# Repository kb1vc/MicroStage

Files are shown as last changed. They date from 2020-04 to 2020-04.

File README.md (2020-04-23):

# Description:

  Micro-positioning stage. 
 
  Author: Matt Reilly

  A simple sliding table that can be positioned via a 4-40 or M3 screw. 
  
  It requires a 3D printer and a Flavia stick.  The stick is used for
  the linear bearing.  Other things might suffice, but I had some of
  these around.  

  This is what a Flavia stick looks like: 
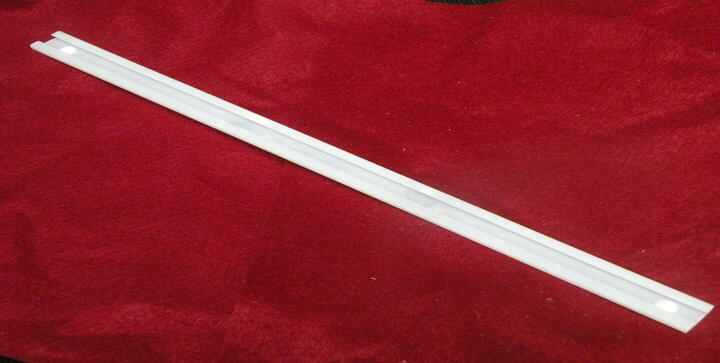
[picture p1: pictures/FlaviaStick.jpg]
A Flavia Stick
  
  
  This is a single-axis version of the micro positioning stage. 
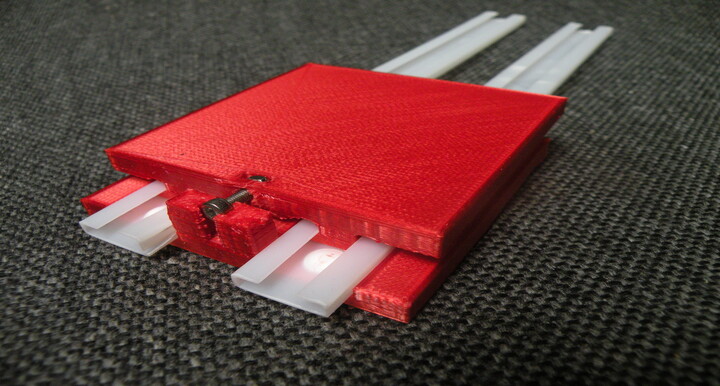
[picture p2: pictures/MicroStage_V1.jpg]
The Stage
  

  And here is an XY positioner.  
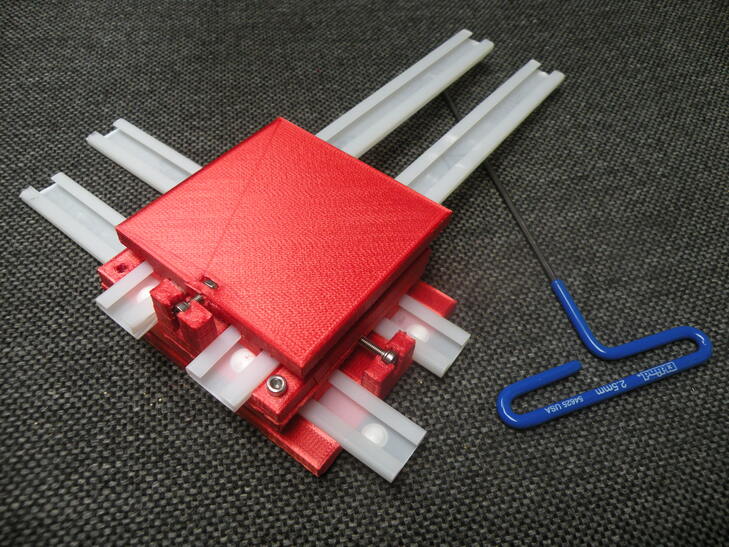
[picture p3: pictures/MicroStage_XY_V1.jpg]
XY Positioner
  
  
# The Source

The source for the components is in OpenSCAD (http://www.openscad.org). It 
is better than STL for distribution, as normal humans can read and write it.

I try to provide some commentary in the source code where things aren't 
obvious or where I expect you'd want to make some changes.  Most of the
good comments are in Common.scad where all the dimensions are defined. 

# Printing

The prototypes and test widgets were printed on a Monoprice Maker Select Plus
using Silk PLA at 230C. The slide was printed flat side up, sitting on the four 
feet. This provides better dimensional control of the horizontal parts of 
the feet which must fit nicely inside the Flavia sticks. 

I used Cura version 3.6 for the slicer. (Yes, I know they're on to newer 
versions, but 3.6 works and I don't have to worry about losing a lot of
configuration data.)  The infill density was 30% and the support density 
was 10%.  YMMV and I didn't do an exhaustive study to find the perfect
combination.  

# Dimensions

All dimensions are in inches, since that's what I have in the way of
calipers.  Yes, it is kinda 19th century, but I've got a 21st century
computer in front of me that can multiply and divide by 25.4. 

That said, the models here are all set up for M3-0.5 screws.  That gets
you 500 microns per turn of the setscrew. Skip the coffee tomorrow morning
and you might get 10 micron resolution.  If you are reading this in 
black and white, then you may only have access to imperial hardware. 
A 4-40 screw and nut will work just fine. You'll get about 25 mils per turn
which ain't so bad for something you made in your basement. 

# Assembly

Pretty much as in the picture.  (See the picture. The background is the
seat cushion on my lab chair. Sometimes I use red felt, but the shiny 
red plastic doesn't show up so well.)  The design files here have added 
mounting holes at the corners of the base and slide.  This allows you to 
bolt a Y axis base onto an X axis slide, giving you *two* dimensions to 
fiddle.

I've found that cyanoacrylate will hold the Flavia sticks to the PLA. 
I wouldn't [hang a man in a hardhat from it,](https://www.youtube.com/watch?v=sZB7sO5ZoV8) but the bond is serviceable. 

# Performance

This is not a laboratory grade device.  It does work. (Or at least the single
axis version works.  The printer isn't done with the second set of parts yet.)
The lash in the movement isn't going to worry the folks at
Starrett any time soon.  If you obsess about such things, turn the
drive screw CCW to push the table *away* from the riser block.  Then turn
the screw head CW to draw the table *toward* the riser block. That
will probably get you the smoothest motion. 

If that isn't adequate, then a trip to Ebay will probably get you 
something that even the most discerning user would find suitable. 

There is no displacement indicator -- an indicator is superfluous for my 
purposes.  If it is important to you, I would encourage you to either
1. Design a solution and try it out.  When it works, post it to github. 
2. Take a look on Ebay where you will probably find something that 
even the most discerning user would find suitable. 

The travel is limited to the length of the "leadscrew."  The assortment
I bought from the "High Precision Machine Parts and Screen Door Company of Guangzhou" topped out at 20mm.  However, [Grainger](https://www.grainger.com/product/FABORY-M3-0-50mm-Machine-Screw-38EA26) has graciously offered to supply
me with 50mm screws for a modest charge. I suspect you could make 
similar arrangements. 

# Q and A

**Q:** Why a normal screw and not a threaded rod?

**A:** A threaded rod would be ideal, but small diameter threaded rod is hard to find. Much of the stuff you find on Amazon and other places will be threaded at the ends.  (I think the intended use is for servo linkages.)  One could thread a rod with things found around the house, but life expectancies being what they are, I can't see it myself. 

**Q:** Why is it so small? 

**A:** I wanted this to be easy to print. This fits on every 3D printer that I know. 

**Q:** How long will this take to print? 

**A:** It all depends on your printer.  I printed both pieces on my well-worn Monoprice Select Plus at 0.15mm resolution in a little over 4 hours. 

**Q:** Why a pocket for the lead screw head, rather than a hole. 

**A:** Materials, variations in printer quality, phase of moon, and a 
million other things conspire to make close tolerances hard to achieve with
a typical home 3D printer.  Since
the hole in the base block would need to line up pretty closely with the
hole in the slide, all of those variations would need to be controlled. 
Counting on that is just bad engineering. 

When you hear someone say "the device is built to exacting tolerances: 
every part must be *exactly* the right size" you are either hearing 
* someone who is talking through their pants
* a sales pitch for a luxury item whose cost and price appeal to a certain kind of person
* a description of a precision device that you will never be able to afford
* a story about crap engineering by people who are too lazy to think about reality and are willing to either endure lots of rejects at the end of the line, or are going to use you for "quality" control. 

Good engineering will design within the capabilities of the technology and
the properties of the material.  I'm not a professional Mech-E, but I respect
them enough to at least *try*. 

**Q:** Will this work with ABS? PETG? Mother-of-pearl? 

**A:** I haven't tried it.  Someone should. (Well, maybe not with mother-of-pearl.)

**Q:** Why do this? 

**A:** I've got a 3D printer.  You've probably got a 3D printer.  How many tiny plastic boats does one person *need*?

**Q:** How can I prepare for an exciting career in the world of mobile pet grooming? 

**A:** I can't help you there. 

# License
See the LICENSE file for copyright and conditions for re-use.

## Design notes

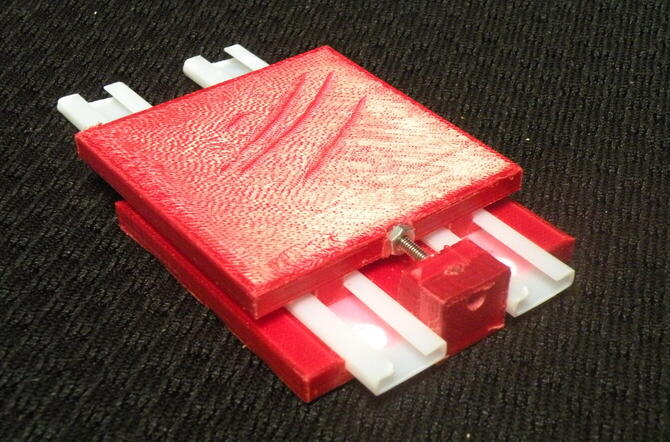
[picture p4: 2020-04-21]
pictures/MicroStage_V0.jpg

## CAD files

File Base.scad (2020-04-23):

include <Common.scad>

module BaseBlock() {
   cube([BaseW, BaseL, BaseT], center=true);
}

module Slot() {
   // a box around a flavia stick
   translate([0, 0, SlotZ]) {
      cube([FlaviaOW, BaseL * 1.1, FlaviaOH], center=true);
   }
}

module ScrewSlot(screw_dia, head_dia, head_depth, driver_dia, height) {
   // cut a slot (rather than a hole) in the riser block
   // to hold the leadscrew.  The leadscrew head will "float"
   // in the Z direction, relative to the slide to relieve
   // binding.
   //
   // There are three parts: the slot for the leadscrew threaded
   // part, the slot for the head, and the slot for the driver.
   //
   // For now, we'll do the metric M3 capscrew
   //
   // This slot is -- subtracted -- from the riser body.
   
   // The screw slot
   translate([0, 0.5 * height, 0]) cube([screw_dia, height, height], center=true);
   // the head slot
   cube([head_dia, head_depth, height], center=true);   
   // the driver slot
   translate([0, -0.5 * height, 0]) cube([driver_dia, height, height], center=true);
}


module RiserBlock() {
   difference() {
     cube([RiserW, RiserD, RiserH], center=true);
     union() {
       translate([0,0,RiserLeadScrewCenter - 0.5 * RiserH]) {
         ScrewSlot(RiserScrewHole, HeadSlotM3, HeadDM3, ShankM3, RiserD * 3);
       }
     }
   }
}

module Base() {
   translate([0,-0.5 * (BaseL - RiserD),0.5 * RiserH])
       RiserBlock();
   translate([0,0,0.5*BaseT])
   difference() {
       BaseBlock();	        
       union() { 
         translate([SlotSp * 1, 0, 0]) Slot();
         translate([-SlotSp * 1, 0, 0]) Slot();
	 MountingHoles();
       }
   }
}

scale([25.4,25.4,25.4]) {
 Base();
}

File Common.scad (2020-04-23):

// All dimensions in inches


$fn=32;

FlaviaOH = 0.185;
FlaviaIH = 0.11;
FlaviaOW = 0.71;
FlaviaIW = 0.55;
FlaviaSlotW = 0.27;
FlaviaMatThick = 0.032;

BaseT = 0.25;
BaseW = FlaviaOW * 4;
// for Test
// BaseL = 0.5;
BaseL = BaseW;



RiserW = BaseW * 0.25;
RiserD = 0.25;
RiserScrewHole = 0.135; // oversize for 0.1285

RiserScrewSlotW = 0.2;
RiserScrewSlotD = 0.2;
RiserScrewHeadDia = 0.25; // panhead 

SlotZ = BaseT - FlaviaOH + FlaviaMatThick;   

TeeH = 1.2 * FlaviaOH; // just to say

// When sitting in slide
SlideHeight = SlotZ + FlaviaMatThick + TeeH + BaseT;
RiserH = SlideHeight * 1.2;
RiserLeadScrewCenter = RiserH - (BaseT * 0.5);
SlideLeadScrewCenter = SlideHeight - (SlotZ + FlaviaMatThick) - (BaseT * 0.5);

SlotSp = FlaviaOW;

// remembering that everything is in inches.  (how embarassing)

Smidge = 0.025; // nearest metric is 0.6 mm.

// The original design said this: 
//   captive nuts need to be a tight (interference) fit in the
//   slot, as the difference between the longest and shortest chord
//   can be quite small (0.030 in the case of a 4-40 nut)
//   Both slot widths will be tight and require an "arbor press."
//   In the absence of an arbor press, one may use a thumb and a
//   coin.
//
// The original design was broken.
//
//   The captive nuts need to float a bit.  The pocket "depth" should
// be a little loose, even though we pay for this with a bit of lash.
//
//   Additionally, the screw head floats in a slot. This allows some
// freedom to align the screw in the base slot with the hole in the slide.
// Dimensional tolerances make lining up the holes between the base riser
// block and the slide platform difficult and fragile.  Small changes in
// printer resolution or the phase of the moon can cause the two holes
// not to line up.  So, the head floats.
// 
NutPocketW4_40 = 0.240;  // captive nut "dia" for 4-40 nut
NutPocketWM3 = 0.210;    // captive nut "dia" for M3 nut

NutPocketDepth = 0.095 + Smidge;

// In places where we need a little bit of play,
// this is our delta 


// The head slot widths need to be just a bit oversized,
// as we'd like most of the friction to be in the anti-lash
// part of the slot.
HeadSlot4_40 = 0.225 + Smidge; // head dia for 4-40 pan head
HeadSlotM3 = 0.21 + Smidge; // head dia for M3 cap screw

// This needs to be a little snug, but not tight.
// The difference in fit amounts to the lash in the
// system.  In general, I'd rather not care, and require
// "one direction only" movement of the slide.  But
// one should never foreclose opportunities for redemption
// (going a little bit too far). 
HeadD4_40 = 0.065 ; // head depth for 4-40 pan head
HeadDM3 = 0.120; // head depth for M3 cap screw

// A driver (either metric 2.5mm or imperial
Shank4_40 = 0.170 ;
ShankM3 = 0.150; // give a little bit for mis-alignment.

MountingHoleOffset = 0.2;
MountingHoleDia = RiserScrewHole;

module ScrewHole() {
  cylinder(d=RiserScrewHole, h = 10, center=true);
}

module MountingHoles() {
  // holes in the base and slide to allow the Y axis base to bolt
  // to the X axis slide
  // four corners.
  X = BaseW * 0.5 - MountingHoleOffset;
  Y = BaseL * 0.5 - MountingHoleOffset;  
  translate([X, Y, 0]) ScrewHole();
  translate([X, -Y, 0]) ScrewHole();  
  translate([-X, Y, 0]) ScrewHole();
  translate([-X, -Y, 0]) ScrewHole();  
}

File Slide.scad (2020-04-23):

include <Common.scad>

module Nut(min_chord, depth) {
  // radius of minimal enclosing circle is
  r = min_chord  / sqrt(3) ; // angles in degrees.
  echo("min_chord ", min_chord, " rad " , r, " cos 30 ", cos(30));
  points = [ 
    for(angle = [30:60:350]) [ cos(angle) * r, sin(angle) * r ]
    ];

  echo(depth);
  echo(points);
  linear_extrude(depth) { polygon(points); }
}

// Add captive nut pocket
module NutPocket(nut_dia, nut_thickness, screw_dia) {
  translate([-0.5*nut_dia, -nut_thickness, -2]) cube([nut_dia, nut_thickness, 10]);
  rotate([90,0,0])  {
    // stack a cube slot above it, baseline on yz plane
    //translate([-0.5*nut_dia, 0, -2])
    //  cube([nut_dia, 10, nut_thickness]);    // Add the screw hole
    cylinder(d=screw_dia, h = 1000, center=true);
  }
}

module SlideBlock() {
   translate([0,0,0.5*BaseT]) cube([BaseW, BaseL, BaseT], center=true);
}

module Tee() {
  // fits in the flavia stick slot
  union() {
    translate([0,0,0.5* FlaviaIH]) cube([FlaviaIW, BaseL, FlaviaIH], center=true);
    translate([0,0,0.5*TeeH]) cube([FlaviaSlotW, BaseL, TeeH], center=true);
  }
}

module TeePair() {
  difference() {
    union() {
      translate([SlotSp * 1, 0, 0]) Tee();
      translate([-SlotSp * 1, 0, 0]) Tee();
    }
    cube([BaseW, BaseL - 1.0,3*TeeH], center=true);
  }	
}

 
module LeadScrewHole() {
  translate([0,0,SlideLeadScrewCenter]) 
    rotate([90,0,0])
      cylinder(d=RiserScrewHole,h=2*BaseL, center=true);
}

module Slide() {
  difference() {
     union() {
       translate([0,0,TeeH - 0.001]) SlideBlock();	        
       TeePair();
     }
     union() {
       translate([0, 0.5*BaseL - NutPocketDepth, SlideLeadScrewCenter]) NutPocket(NutPocketWM3, NutPocketDepth, RiserScrewHole);
       MountingHoles();
     }
  }
}

scale([25.4,25.4,25.4]) {
  Slide();
}

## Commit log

2020-04-21 V0 commit
    [Base.scad, Common.scad, Slide.scad]
2020-04-23 Added pocketed nut and a slot for the screw head. The latter has been done to allow the screw to "float" relative to the sliding table. This eliminates the fiddly tolerance stuff around aligning the 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
    Added mounting holes at the corners of base and slide. This allows the
    base of a Y-axis set to mount to the slide on an X-axis stage. Hot diggity!
    Two dimensions.
    [Base.scad, Common.scad, Slide.scad]
